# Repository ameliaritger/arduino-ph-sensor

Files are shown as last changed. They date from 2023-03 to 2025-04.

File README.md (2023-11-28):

# Arduino pH sensor 

pH sensor in the rocky intertidal during sunset

## What's in this repository?
This repository contains the scripts and files related to the development of an intertidal Arduino pH sensor.

This repository is maintained by Hofmann Lab graduate student Amelia Ritger (GitHub: [@ameliaritger](https://github.com/ameliaritger)) at the University of California, Santa Barbara in the Department of Ecology, Evolution, & Marine Biology. Please direct any questions or comments about this repository to [Amelia Ritger](mailto:aritger@ucsb.edu).

## How is this repository structured?
```
.
├── documentation/                              # folder containing documentation for building the Arduino data logger for the pH sensor project
│   └── arduinoPHConstructionOperation.docx     # document for building the Arduino data logger
|
├── software/                                   # folder containing software relevant to the Arduino data logger
|   └── arduinoCode/                            # folder containing C++ code to program the Arduino
|      └── CONFIG.h                             # configuration script, to set filename, sampling interval, and sampling start date & time
|      └── SRC.h                                # source script, for useful functions
|      └── arduinoCode.ino                      # main script, to sample from the pH sensor and store the values on the Arduino
|           
|   └── rCode/                                  # folder containing R code to process pH sensor data. Note: currently formatted for project development, not finalized for public application!
|      └── Final_OMEGAS.Rmd                     # Step 3: Apply calibration constants to deployment data
|      └── Final_Tris_Cal.Rmd                   # STEP 2: Calculate calibration constants for the sensor
|      └── Final_deploy_voltages.Rmd            # STEP 4: Plot calibrated sensor data with HOBO logger temperature data
|      └── Final_standardize_data.Rmd           # STEP 1: Standardize Arduino (new design) and Madgetech (old design) data
|
├── media/                                      # folder containing media files for project repo
|
├── draft_files/                                # folder containing all draft project files related to initial testing and development
|
├── README.md
├── .gitignore        
└── ph-sensor-dev.Rproj
```

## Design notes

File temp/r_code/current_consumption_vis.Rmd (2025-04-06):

---
title: "Data vis current consumption Version 2"
author: "Amelia Ritger"
date: "2023-10-15"
output: html_document
---

```{r setup, include=FALSE}
knitr::opts_chunk$set(echo = TRUE)
library(tidyverse)
library(janitor)
library(here)
library(ggstar)
```

Plot when adalogger is wirelessly communicating (reed switch triggered 3x) - 1) receiving data, 2) sending data, and 3) receiving data 
```{r}
receive_all <- read_csv(here("temp", "data", "power", "VoltageSet3_60V_at2023_10_14_12_19_57.csv")) %>%
  clean_names() %>%
  mutate(current_ma = current_a*10) %>%
  select(1:3, current_ma)

ggplot(receive_all, aes(x=times_s, y=current_ma)) +
  geom_line()
```

Plot "Run 1" - when Adalogger is receiving interval data
```{r}
receive_int <- read_csv(here("temp", "data", "power", "VoltageSet3_60V_at2023_10_14_12_25_20.csv")) %>%
  clean_names() %>%
  mutate(current_ma = current_a*10) %>%
  select(1:3, current_ma)

ggplot(receive_int, aes(x=times_s, y=current_ma)) +
  geom_line() +
  scale_y_continuous(limits = c(0.1,0.4),
                    breaks = seq(0, 100, by = 0.05))
```

Plot "Run 2" - when Adalogger is sending "no new data to report"
```{r}
send_no_new <- read_csv(here("temp", "data", "power", "VoltageSet3_60V_at2023_10_14_12_27_18.csv")) %>%
  clean_names() %>%
  mutate(current_ma = current_a*1000) %>%
  select(1:3, current_ma) %>%
  filter(times_s < 55) %>%
  mutate(times_s = times_s - 10) %>%
  filter(times_s>0)

receive_avg <- send_no_new %>%
  filter(times_s > 20,
         times_s < 49) %>%
  summarize(mean = mean(current_ma))  

annotation <- data.frame(
   x = c(25.56629),
   y = c(40),
   label = c("37.5 mA")
)

ggplot(send_no_new, aes(x=times_s, y=current_ma)) +
  annotate(geom = "point", x = 35.56629-10, y = 37.55524, colour = "#0072B2", size = 3) +
  geom_line() + 
  geom_text(data=annotation, aes( x=x, y=y, label=label), color="black", size=5, fontface="bold", hjust=-0.15) +
  labs(x="Time (s)", y="Current (mA)") +
  scale_y_continuous(limits = c(10,40),
                    breaks = seq(0, 100, by = 5)) +
  theme_bw() +
  theme(text = element_text(size=20))

#ggsave(here("temp", "figures", "OCEANS", "receive_data.png"), height=10, width=15, units="cm")
```

Plot "Run 3" - when Adalogger is sending  SD card data
```{r}
send_sd_a <- read_csv(here("temp", "data", "power", "VoltageSet3_60V_at2023_10_14_12_31_23.csv")) %>%
  clean_names() %>%
  mutate(current_ma = current_a*10) %>%
  select(1:3, current_ma)

ggplot(send_sd_a, aes(x=times_s, y=current_ma)) +
  geom_line() +
    scale_y_continuous(limits = c(0.1,0.4),
                     breaks = seq(0, 100, by = 0.02)) 
```

Plot "Run 4" - another ex of when Adalogger is sending SD card data
```{r}
send_sd_b <- read_csv(here("temp", "data", "power", "VoltageSet3_60V_at2023_10_14_12_34_55.csv")) %>%
  clean_names() %>%
  mutate(current_ma = current_a*1000) %>%
  select(1:3, current_ma) %>%
  filter(times_s<40)

send_avg <- send_sd_b %>%
  filter(times_s > 10,
         times_s < 19) %>%
  summarize(mean = mean(current_ma))  

annotation <- data.frame(
   x = c(31.83300, 10),
   y = c(40, 39),
   label = c("38.8 mA", "32.1 mA")
)

ggplot(send_sd_b, aes(x=times_s, y=current_ma)) +
  annotate(geom = "point", x = 31.83300, y = 38.80183, colour = "#0072B2", size = 3) +
  annotate(geom = "point", x = 11.6510231, y = 32.11241, colour = "#0072B2", size = 3) +
  geom_line() + 
  geom_text(data=annotation, aes( x=x, y=y, label=label), color="black", size=5, fontface="bold", hjust=-0.15) +
  labs(x="Time (s)", y="Current (mA)") +
  scale_y_continuous(limits = c(10,40),
                    breaks = seq(0, 100, by = 5)) +
  theme_bw() +
  theme(text = element_text(size=20))

#ggsave(here("temp", "figures", "OCEANS", "send_sd.png"), height=10, width=15, units="cm")
```

Plot when Adalogger is sampling and then sleeping
```{r}
sample_sleep_a <- read_csv(here("temp", "data", "power", "VoltageSet3_60V_at2023_10_14_14_30_00.csv")) %>%
  clean_names() %>%
  mutate(current_ma = current_a*1000) %>%
  select(1:3, current_ma) %>%
  filter(times_s>8) %>%
  mutate(times_s = times_s - 8) %>%
  filter(times_s<25)

sleep <- sample_sleep_a %>%
  filter(times_s > 5.5,
         times_s < 18.5) %>%
  summarize(mean = mean(current_ma))

sample <- sample_sleep_a %>%
  filter(times_s > 3.5,
         times_s < 5.3) %>%
  summarize(mean = mean(current_ma))

annotation <- data.frame(
   x = c(5.5,20.5, 9.95),
   y = c(0.156*100,0.135*100, 0.027*100),
   label = c("15.5 mA", "13.2 mA", "1.8 mA")
)

ggplot(sample_sleep_a, aes(x=times_s, y=current_ma)) +
  annotate(geom = "point", x = 5.4593306, y = 0.15447820*100, colour = "#0072B2", size = 3) +
  annotate(geom = "point", x = 19.884166, y = 0.13227690*100, colour = "#0072B2", size = 3) +
  annotate(geom = "point", x = 9.9521229, y = 0.01827854*100, colour = "#0072B2", size = 3) +
  geom_line() + 
  geom_text(data=annotation, aes( x=x, y=y, label=label), color="black", size=5, fontface="bold", hjust=-0.15) +
  labs(x="Time (s)", y="Current (mA)") +
  scale_y_continuous(limits = c(0,16),
                     breaks = seq(0, 100, by = 4)) +
  theme_bw() +
  theme(text = element_text(size=20))

#ggsave(here("temp", "figures", "OCEANS", "sample-sleep.png"), height=10, width=15, units="cm")
```

Plot another example of when Adalogger is sampling and then sleeping
```{r}
sample_sleep_b <- read_csv(here("temp", "data", "power", "VoltageSet3_60V_at2023_10_14_14_54_39.csv")) %>%
  clean_names() %>%
  mutate(current_ma = current_a*10) %>%
  select(1:3, current_ma) %>%
  filter(times_s<20)

annotation <- data.frame(
   x = c(14.5,4.5),
   y = c(0.16,0.15),
   label = c("0.155 mA", "0.147 mA")
)

ggplot(sample_sleep_b, aes(x=times_s, y=current_ma)) +
  annotate(geom = "point", x = 14.3918459, y = 0.15507400, colour = "#56B4E9", size = 3) +
  annotate(geom = "point", x = 4.4597836, y = 0.14704890, colour = "#56B4E9", size = 3) +
  annotate(geom = "point", x = 7.0232589, y = 0.02732002, colour = "#56B4E9", size = 3) +
  geom_line() + 
  geom_text(data=annotation, aes( x=x, y=y, label=label), color="black", size=5, fontface="bold", hjust=-0.2) +
  labs(x="Time (s)", y="Current (mA)") +
  theme_bw() +
  theme(text = element_text(size=20))
```

Merge all the plots into one!
```{r}
send_sd_b <- send_sd_b %>%
  filter(times_s < 34.739158)

send_no_new <- send_no_new %>%
  filter(times_s > 2.37331581)

all_list <- rbind(sample_sleep_a, send_sd_b, send_no_new) %>%
  mutate(time_diff = abs(times_s - lag(times_s, default = first(times_s))),
         time_diff = ifelse(time_diff > 1, 0.171, time_diff),
         time_adjust = accumulate(time_diff[-1], sum, .init = times_s[1])) %>%
  # if current_ma is less than 2, subtract 0.5697
  mutate(current_ma = ifelse(current_ma < 2, current_ma - 0.5697, current_ma)) %>%
 # if current_ma is greater than 10 and less than 15, and times_s is less than 25, subtract 0.5
  mutate(current_ma = ifelse(current_ma > 10 & current_ma < 15 & time_adjust < 25, current_ma - 0.606, current_ma))
  
annotation <- data.frame(
   x = c(15, 7, 89,56.69334, 30),
   y = c(17, 5, 39.5, 40, 25),
   label = c("12.8 mA", "1.3 mA", "37.5 mA", "38.8 mA", "32.1 mA")
)

#overwrite in-between periods with 1.26 mA sleep current 
all_list_adjust <- all_list %>%
  mutate(current_ma = ifelse(time_adjust > 24.03231 & time_adjust < 28.29884, 1.26, current_ma),
         current_ma = ifelse(time_adjust > 61.70909 & time_adjust < 66.31044, 1.26, current_ma),
         current_ma = ifelse(time_adjust > 99.10344, 1.26, current_ma))

#import image of lightning bolt
#lightning_icon <- ggimage::image_read2(here("temp", "figures", "fa-bolt.png"))

ggplot(all_list_adjust, aes(x=time_adjust, y=current_ma)) +
  annotate("rect", xmin = 2, xmax = 23, ymin = 0, ymax = 40, alpha = .1,fill = "black") +
  annotate("rect", xmin = 27, xmax = 63, ymin = 0, ymax = 40, alpha = .1,fill = "black") +
  annotate("rect", xmin = 65, xmax = 100, ymin = 0, ymax = 40, alpha = .1,fill = "black") +
  annotate("label", x = 12.5, y = 35, label = "A", fontface="bold", size = 7) +
  annotate("label", x = 45, y = 5, label = "B", fontface="bold", size = 7) +
  annotate("label", x = 82, y = 5, label = "C", fontface="bold", size = 7) +
  annotate(geom = "point", x = 56.69334, y = 38.80183, colour = "#0072B2", size = 3) +
  annotate(geom = "point", x = 36.51136, y = 32.11241, colour = "#0072B2", size = 3) +
  annotate(geom = "point", x = 82.96347, y = 37.55524, colour = "#0072B2", size = 3) +
  annotate(geom = "point", x = 19.719877, y = 12.760250, colour = "#0072B2", size = 3) +
  annotate(geom = "point", x = 9.952123, y = 1.258154, colour = "#0072B2", size = 3) +
  geom_line() + 
  geom_text(data=annotation, aes( x=x, y=y, label=label), color="black", size=5, fontface="bold", hjust=-0.15) +
  labs(x="Time (s)", y="Current (mA)") +
  scale_y_continuous(limits = c(0,40),
                    breaks = seq(0, 100, by = 5)) +
  theme_bw() +
  theme(text = element_text(size=20)) +
  #annotate("text", x = 40, y = 10, label = "Reed switch activated", fontface="bold", size = 5, hjust = 0) +
  #annotate("segment", x = 38, xend = 29, y = 8, yend = 1.5, arrow = arrow(length = unit(0.5, "cm"))) +
  geom_star(x=26.8, y=4, starshape=26, angle = -30, fill="#D55E00", size=5, colour = NA) +
  geom_star(x=64.8, y=4, starshape=26, angle = -30, fill="#D55E00", size=5, colour = NA)

#ggsave(here("temp", "figures", "FINAL(diss)", "current.png"), height=10, width=30, units="cm")
```

```{r}
sample_jan <- read_csv(here("temp", "data", "power", "VoltageSet3_6V_at2024_01_28_13_52_14.csv")) %>%
  clean_names() %>%
  mutate(current_ma = current_positive_a*1000) %>%
  select(1:2, current_ma)

ggplot(sample_jan, aes(x=times_s, y=current_ma)) +
  #annotate(geom = "point", x = 14.3918459, y = 0.15507400, colour = "#56B4E9", size = 3) +
  #annotate(geom = "point", x = 4.4597836, y = 0.14704890, colour = "#56B4E9", size = 3) +
  #annotate(geom = "point", x = 7.0232589, y = 0.02732002, colour = "#56B4E9", size = 3) +
  geom_line() + 
  #geom_text(data=annotation, aes( x=x, y=y, label=label), color="black", size=5, fontface="bold", hjust=-0.2) +
  labs(x="Time (s)", y="Current (mA)") +
  theme_bw() +
  theme(text = element_text(size=20))

sample_sleep <- sample_jan %>%
  mutate(state = ifelse(current_ma < 1.4, "sleep", 
                        ifelse(current_ma > 22, "radio", 
                               ifelse(current_ma> 10 & current_ma < 13, "sample", "other"))),
         state = ifelse(times_s > 125 & times_s < 127, "other", 
                        ifelse(times_s > 152 & times_s < 154, "other", 
                               ifelse(times_s > 182 & times_s < 185, "other", state)))) %>%
  filter(times_s>50) %>% 
  #remove last 2 data points
  slice(1:(n()-2))
  # if times_s is 125 - 127, 152-154, or 182-185 then label as "other" state

sample_sleep_group <- sample_sleep %>%
  group_by(state) %>%
  summarize(mean_current = mean(current_ma)) %>%
  ungroup() # 1.26 mA = sleep

ggplot(sample_sleep, aes(x=times_s, y=current_ma)) +
  #geom_line() + # color by sleep
  geom_point(aes(color = state)) +
  geom_line() +
  labs(x="Time (s)", y="Current (mA)") +
  theme_bw() +
  theme(text = element_text(size=20))
```

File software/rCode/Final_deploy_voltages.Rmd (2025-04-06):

---
title: "STEP 4: Plot ALL calibrated data against HOBO temperature data"
author: "Amelia Ritger"
date: "2023-04-07"
output: html_document
---

```{r setup, include=FALSE}
knitr::opts_chunk$set(echo = TRUE)
```

##Load libraries, set constants
```{r}
library(tidyverse)
library(readr)
library(janitor)
library(here)
library(lubridate)
library(scales)
library(ggpmisc)

file_names <- list.files(here("temp", "data", "raw", "deploy"), pattern = "CLEAN", recursive = FALSE, full.names = TRUE)

merged <- read_csv(file_names, col_names = TRUE) %>%
  mutate(date_lubridate=mdy(date)) %>% # tell R "date" is a DATE
  mutate(time_lubridate=hms(time)) %>% # tell R "time" is a TIME
  unite(date_time, c(date, time), sep = " ", remove = TRUE) %>% # combine the date and time columns
  mutate(date_time_lubridate=mdy_hms(date_time),
         date_time = round_date(date_time_lubridate, "5 mins")) %>%
  filter(date_time > ymd_hms("2022-12-15 17:00:00")) %>%
  mutate(v1corr = ifelse(logger=="arduino", v1-11.2, v1),
         v4corr = ifelse(logger=="arduino", v4-1.3,v4))

merged_corr_sum <- merged %>%
  group_by(logger) %>%
  summarize(meanT = mean(v4corr),
            rangeT = max(v4) - min(v4),
            meanP = mean(v1corr),
            rangeP = max(v1) - min(v1),
            sdT = sd(v4),
            sdP = sd(v1))

merged_diff <- merged %>%
  arrange(date_time) %>%
  mutate(diff_lag = abs(v4-lag(v4, default = first(v4))),
         diff_time = date_time-lag(date_time, default = first(date_time)),
         diff_temp = v4-lag(v4, default=first(v4)),
         diff_ph = v1-lag(v1, default=first(v1))) %>%
  filter(!diff_ph == 0) %>%
  group_by(logger) %>%
  summarize(meanT = mean(diff_temp),
            meanP = mean(diff_ph),
            sdT = sd(v4),
            sdP = sd(v1))

avgT <- (merged_corr_sum[[1,2]] + merged_corr_sum[[2,2]]) / 2
avgP <- (merged_corr_sum[[1,4]] + merged_corr_sum[[2,4]]) / 2

diffT <- merged_corr_sum[[1,2]] - merged_corr_sum[[2,2]]
diffP <- merged_corr_sum[[1,4]] - merged_corr_sum[[2,4]]

sd1a <- merged_diff$sdT[1]
sd1m <- merged_diff$sdT[2]

ggplot(merged, aes(x=date_time)) +
  geom_line(aes(y=v4, color=logger),size=1) +
  geom_ribbon(aes(ymin = v4 - ifelse(logger=="arduino", sd1a, sd1m), ymax = v4 + ifelse(logger=="arduino", sd1a, sd1m), fill=logger), alpha=0.2, show.legend=FALSE) +
  scale_color_manual(values=c("#D55E00", "#0072B2"), 
                     labels = c("New Design", "Old Design")) +
  scale_fill_manual(values=c("#D55E00", "#0072B2"), 
                     labels = c("New Design", "Old Design")) +
  #scale_color_brewer(palette="Set1", direction=-1, labels = c("New Design", "Old Design")) +
  #scale_fill_brewer(palette="Set1", direction=-1, labels = c("New Design", "Old Design")) +
  labs(x="Date and Time", y="Temperature (mV)", color = "") +
  scale_x_datetime(breaks = scales::date_breaks("4 hours"), 
                   labels = date_format("%d %b %Y %H:%M")) +
  theme_bw() +
  theme(axis.text.x=element_text(angle=20, vjust = 1, hjust=1),
        legend.position = "top", 
        legend.text = element_text(size=10))

#ggsave(here("temp", "figures", "FINAL(diss)", "temp-deploy.png"), height=10, width=15, units="cm")
```

```{r}
#Subset it for the swap time
merged_diff <- merged %>%
  arrange(date_time) %>%
  mutate(diff_lag = abs(v4-lag(v4, default = first(v4))),
         diff_time = date_time-lag(date_time, default = first(date_time)),
         diff_temp = v4-lag(v4, default=first(v4)),
         diff_ph = v1-lag(v1, default=first(v1))) %>%
  filter(!diff_ph == 0) #%>%
  #group_by(logger) %>%
  summarize(meanT = mean(diff_temp),
            meanP = mean(diff_ph),
            sdT = sd(v4),
            sdP = sd(v1))

ggplot(merged_diff, aes(x=date_time)) +
  geom_point(aes(y=diff_ph, color=logger))
```

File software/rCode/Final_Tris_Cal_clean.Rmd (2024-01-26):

---
title: "STEP 2: Calculate Tris calibration constants for DuraFET"
author: "Amelia Ritger"
date: "2024-01-25"
output: html_document
---

```{r setup, include=FALSE}
knitr::opts_chunk$set(echo = TRUE)
```

##Load libraries, set constants
```{r}
library(tidyverse)
library(readr)
library(janitor)
library(here)
library(lubridate)

filename <- "0125tris_clean" #filename for tris data
row_remove <- 15 # number of rows to remove from beginning of data frame
```

## Run "Ideal" calibration for DuraFET
```{r}
var_ard <- 0 #calculated uncertainties using raw data

ard_correction_m <- 1 #slope coefficient for arduino (corrected with HOBO)
ard_correction_b <- 0

trisdata <- read_csv(here("temp", "data", "jan2024", paste(filename,".csv",sep=""))) %>%
  mutate(date = mdy(date),
           time = hms(time),
           date_time = paste(date, time),
           date_time_lubridate=ymd_hms(date_time)) %>%
  select(date_time_lubridate, v1, v2, v3, v4) %>%
  rename(date_time = date_time_lubridate)

tris_voltages <- data.frame(trisdata$v1,trisdata$v2,trisdata$v3,trisdata$v4) %>% # create OMEGAS data frame with the raw voltages
  mutate(mv1=as.numeric(trisdata.v1),
         mv2=as.numeric(trisdata.v2),
         mv3=as.numeric(trisdata.v3),
         mv4=as.numeric(trisdata.v4)) %>% # changing data to numeric arguments
  select(mv1, mv2, mv3, mv4) # cleaning data frame

omegas_temp_tris <- tris_voltages %>% # create new data frame using omegas values
  mutate(v1=(mv1/1000),
         v2=(mv2/1000),
         v3=(mv3/1000),
         v4=(mv4/1000)) %>% # converting the mV to volts
  mutate(vbattery=((abs(v3)/100)*101.57)) %>% # calculate vbattery
  mutate(z=(v4/100)+vbattery*((15000*1)/((1000000*1)+(15000*1)))) %>% # calculate column k
  mutate(y=(z*(1000000*1))) %>% # calculate column l
  mutate(rthermistor=(y/(vbattery-z))) %>% # calculate Rthermistor
  mutate(sh_a=as.numeric(0.00106329736674527)) %>% # create column with Steinhart constant A
  mutate(sh_b=as.numeric(0.000251377462346306)) %>% # create column with Steinhart constant B
  mutate(sh_c=as.numeric(2.55455247726963E-08)) %>% # create column with Steinhart constant C
  mutate(k=(1/(sh_a+sh_b*log(rthermistor)+sh_c*(log(rthermistor))^3))) %>% # create column to calculate intermediate value K
  mutate(durafet=as.numeric((k-273.15))) %>% # create new column to calculate durafet therm
  mutate(calt=as.numeric(1.0086*durafet+0.3157)) # create Cal_T column (does not get used for further calibration)

temp <- c(omegas_temp_tris$durafet) # copy durafet therm into tris pH template
b <- as.numeric(rep("11911.08",length(temp))) # create vector for tris pH template column b
c <- as.numeric(rep("18.2499",length(temp))) # create vector for tris pH template column c
d <- as.numeric(rep("0.039336",length(temp))) # create vector for tris pH template column d
e <- as.numeric(rep("366.27059",length(temp))) # create vector for tris pH template column e
f <- as.numeric(rep("0.53993607",length(temp))) # create vector for tris pH template column f
g <- as.numeric(rep("0.00016329",length(temp))) # create vector for tris pH template column g
h <- as.numeric(rep("64.52243",length(temp))) # create vector for tris pH template column h
i <- as.numeric(rep("0.084041",length(temp))) # create vector for tris pH template column i
j <- as.numeric(rep("0.11149858",length(temp))) # create vector for tris pH template column j
k <- as.numeric(rep("273.15",length(temp))) # create vector for tris pH template column k
t <- as.numeric(rep(k+temp),length(temp)) # create vector for tris pH template column t
m <- as.numeric(rep("35",length(temp))) # create vector for tris pH template column m

tris_ph_template <- data.frame(temp,b,c,d,e,f,g,h,i,j,t,k,m)%>% # create tris pH template as a data frame with all above columns
  mutate(n=(b-(c*m)-(d*m*m))*1/t) %>% # create column n
  mutate(o=(-e+(f*m)+(g*m*m))) %>% # create column o
  mutate(p=(h-(i*m))*log(t)-(j*(t))) %>% # create column p
  mutate(trisph=(n+o+p)) # calculate tris pH, add as a new column to tris pH template data frame

omegas_ph_tris <- data.frame(trisdata$date_time,omegas_temp_tris$durafet,omegas_temp_tris$v1) %>% # create data frame with durafet therm and voltage 1 values
  mutate(trisph=tris_ph_template$trisph) %>% # add tris pH values into calibration dataframe 
  mutate(tk=omegas_temp_tris$durafet+273.15) %>% # add TK column to data frame
  mutate(st=(8.31451*tk/96487*log(10))) %>% # add S(T) column to data frame
  mutate(eot=(-0.374911706-(0.001*(tk-290.2751473)))) %>% # add Eo(T) column to data frame
  mutate(omegasph=(omegas_temp_tris$v1-eot)/st) %>% # add pH column to data frame
  mutate(diff=(trisph-omegasph)) %>% # add difference column (tris pH - omegas pH) to data frame
  mutate(tempdiff=abs(omegas_temp_tris.durafet-lag(omegas_temp_tris.durafet,n=5,default=first(omegas_temp_tris.durafet)))) %>% # find difference between two temp measurements 5 rows apart to identify where temperature stabilizes
  mutate(phdiff=abs(omegasph-lag(omegasph,n=5,default=first(omegasph)))) # find difference between two pH measurements 5 rows apart to identify where pH stabilizes

calibration_values <- omegas_ph_tris %>% # work in omegas_calibration dataframe
  filter(row_number()!=c(1:row_remove)) %>% # remove the first 100 rows (first 20 minutes of data)
  slice_min(tempdiff,n=10) %>% # select the rows that contains the minimum values of change in temperature over time 
  slice_min(phdiff,n=1) %>% # select the row that contains the minimum value of change in pH over time in within the 10 lowest temp differences
  mutate(diff_omegasph = (omegasph - mean(omegasph))) %>%
  slice_min(diff_omegasph) %>%
  slice(1L)

#Write out .csv files
write.csv(omegas_ph_tris, here("temp", "data", "jan2024", paste(filename,"_omegas.csv", sep="")),row.names = FALSE) # create csv with calibrated values
write.csv(calibration_values, here("temp", "data", "jan2024", paste(filename,"_omegas_calib.csv", sep="")),row.names=FALSE)
```

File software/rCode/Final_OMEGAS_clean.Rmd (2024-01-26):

---
title: "STEP 3: Apply GREEN and RED calibration data to all readings"
author: "Amelia Ritger"
date: "2023-04-07"
output: html_document
---

```{r setup, include=FALSE}
knitr::opts_chunk$set(echo = TRUE)
```

##Load libraries, set constants
```{r}
library(tidyverse)
library(readr)
library(janitor)
library(here)
library(lubridate)

filename_calib <- "0125tris_clean_omegas_calib" #filename for tris calibration data
filename_deploy <- "0123comp_clean" #filename for deployment calibration data
```

## Run calibration for GREEN data
```{r}
calibration_values <- read_csv(here("temp", "data", "jan2024", paste(filename_calib,".csv",sep=""))) %>%
  rename("durafet_temp" = "omegas_temp_tris.durafet",
         "v1" = "omegas_temp_tris.v1")

rawdata <- read_csv(here("temp", "data", "jan2024", paste(filename_deploy,".csv",sep=""))) %>%
    mutate(date = mdy(date),
           time = hms(time),
           date_time = paste(date, time),
           date_time_lubridate=ymd_hms(date_time)) %>%
  select(date_time_lubridate, v1, v2, v3, v4) %>%
  rename(date_time = date_time_lubridate)

raw_voltages <- data.frame(rawdata$v1,rawdata$v2,rawdata$v3,rawdata$v4) %>% # create OMEGAS data frame with the raw voltages
  mutate(mv1=as.numeric(rawdata.v1),
         mv2=as.numeric(rawdata.v2),
         mv3=as.numeric(rawdata.v3),
         mv4=as.numeric(rawdata.v4)) %>% # changing data to numeric arguments
  select(mv1, mv2, mv3, mv4) # cleaning data frame

omegas_temp_raw <- raw_voltages %>% # create OMEGAS data frame with the raw voltages
  mutate(v1=(mv1/1000),
         v2=(mv2/1000),
         v3=(mv3/1000),
         v4=(mv4/1000)) %>% # converting the mV to volts
  mutate(vbattery=((abs(v3)/100)*101.57)) %>% # calculate vbattery
  mutate(z=(v4/100)+vbattery*((15000*1)/((1000000*1)+(15000*1)))) %>% # calculate column k
  mutate(y=(z*(1000000*1))) %>% # calculate column l
  mutate(rthermistor=(y/(vbattery-z))) %>% # calculate Rthermistor
  mutate(sh_a=as.numeric(0.00106329736674527)) %>% # create column with Steinhart constant A
  mutate(sh_b=as.numeric(0.000251377462346306)) %>% # create column with Steinhart constant B
  mutate(sh_c=as.numeric(2.55455247726963E-08)) %>% # create column with Steinhart constant C
  mutate(k=(1/(sh_a+sh_b*log(rthermistor)+sh_c*(log(rthermistor))^3))) %>% # create column to calculate intermediate value K
  mutate(durafet=as.numeric((k-273.15))) # create new column to calculate durafet therm

temp <- c(omegas_temp_raw$durafet) # copy durafet therm into tris pH template
b <- as.numeric(rep("11911.08",length(temp))) # create vector for tris pH template column b
c <- as.numeric(rep("18.2499",length(temp))) # create vector for tris pH template column c
d <- as.numeric(rep("0.039336",length(temp))) # create vector for tris pH template column d
e <- as.numeric(rep("366.27059",length(temp))) # create vector for tris pH template column e
f <- as.numeric(rep("0.53993607",length(temp))) # create vector for tris pH template column f
g <- as.numeric(rep("0.00016329",length(temp))) # create vector for tris pH template column g
h <- as.numeric(rep("64.52243",length(temp))) # create vector for tris pH template column h
i <- as.numeric(rep("0.084041",length(temp))) # create vector for tris pH template column i
j <- as.numeric(rep("0.11149858",length(temp))) # create vector for tris pH template column j
k <- as.numeric(rep("273.15",length(temp))) # create vector for tris pH template column k
t <- as.numeric(rep(k+temp),length(temp)) # create vector for tris pH template column t
m <- as.numeric(rep("35",length(temp))) # create vector for tris pH template column m

raw_tris_ph <- data.frame(temp,b,c,d,e,f,g,h,i,j,t,k,m) %>% # create tris pH template as a data frame with all above columns
  mutate(n=(b-(c*m)-(d*m*m))*1/t) %>% # create column n
  mutate(o=(-e+(f*m)+(g*m*m))) %>% # create column o
  mutate(p=(h-(i*m))*log(t)-(j*(t))) %>% # create column p
  mutate(trisph=(n+o+p)) # calculate tris pH, add as a new column to tris pH template data frame

omegas_ph_raw <- data.frame(rawdata$date_time,omegas_temp_raw$durafet,omegas_temp_raw$v1) %>%
   # create data frame with durafet therm and voltage 1 values
  rename(date_time=rawdata.date_time) %>% # rename date/time column from trisdata data frame
  mutate(trisph=raw_tris_ph$trisph) %>% # add tris pH values into calibration dataframe TRIS PH IS NOT THE SAME LENGTH AS THE RAW DATA
  mutate(tk=omegas_temp_raw$durafet+273.15) %>% # add TK column to data frame
  mutate(st=(8.31451*tk/96487*log(10))) %>% # add S(T) column to data frame
  mutate(eo=((calibration_values$v1)-(calibration_values$trisph)*8.31451*(273.15+calibration_values$durafet_temp)*log(10)/96487)) %>% # calculate eo value using calibration values
  mutate(eot=(eo-(0.001*(tk-(273.15+calibration_values$durafet_temp))))) %>% # add Eo(T) column to data frame
  mutate(omegasrawph=(omegas_temp_raw$v1-eot)/st) %>% # add pH column to data frame
  mutate(diff=(trisph-omegasrawph)) # add difference column (tris pH - omegas pH) to data frame

raw_calibrated <- omegas_ph_raw %>% # create new dataframe using omegasph_raw data
  select(date_time, omegas_temp_raw.durafet, omegasrawph) %>% # keep only date/time, temperature, and pH columns
  rename("p_h"=3)

#Write .csv
write.csv(raw_calibrated, here("temp", "data", "jan2024", paste("FINAL_arduino.csv")),row.names = FALSE) # create csv with calibrated values

```

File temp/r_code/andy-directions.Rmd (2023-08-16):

---
title: "Untitled"
author: "Amelia Ritger"
date: "2023-04-10"
output: html_document
---

```{r setup, include=FALSE}
knitr::opts_chunk$set(echo = TRUE)
```

fit difference in temperature at each point 

the standard deviation of the temperature in the ICE bath and the 25C bath is what you want to calculate

subtract HOBO temp from Durafet temp, get standard deviation of that. do it for each temperature. 
are there significant differences between each temp.

that's my temperature uncertainty.

Take all my raw data and get the list of file names
```{r}

```

How much can temp change if R1 is at top of the range
```{r}

```

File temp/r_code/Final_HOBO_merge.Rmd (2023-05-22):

---
title: "STEP 4: Plot ALL calibrated data against HOBO temperature data"
author: "Amelia Ritger"
date: "2023-04-07"
output: html_document
---

```{r setup, include=FALSE}
knitr::opts_chunk$set(echo = TRUE)
```

##Load libraries, set constants
```{r}
library(tidyverse)
library(readr)
library(janitor)
library(here)
library(lubridate)
library(scales)
library(ggpmisc)

#pattern_ignore = "calib" #ignore calibration value files
#file_names <- list.files(here("data", "calibrated"), pattern = "*.csv", recursive = FALSE, full.names = TRUE)
#file_ignore <- list.files(here("data", "calibrated"), pattern = pattern_ignore, recursive = FALSE, full.names = TRUE)
#file_names <- setdiff(file_names, file_ignore)

file_names <- list.files(here("data", "calibrated"), pattern = "OMEGAS_CLEAN", recursive = FALSE, full.names = TRUE)

merged <- read_csv(file_names, col_names = TRUE) %>%
  mutate(date_time = round_date(date_time, "15 seconds"))
```

Load and merge hobo logger data
```{r}
temp1 <- read_csv(here("data", "temp", "Apr8_lab.csv"), col_names = TRUE)
temp2 <- read_csv(here("data", "temp", "Apr9_lab.csv"), col_names = TRUE) 
temp4 <- read_csv(here("data", "temp", "Apr12_lab_newhobo.csv"), col_names = TRUE) 
temp5 <- read_csv(here("data", "temp", "Apr11_lab_newhobo.csv"), col_names = TRUE) 
temp6 <- read_csv(here("data", "temp", "Apr10_lab_newhobo_overnight.csv"), col_names = TRUE) 

temp3 <- rbind(temp1, temp2, temp4, temp5, temp6) 

temp <- temp3 %>%
  select(2:3) %>%
  setNames(c("date_time", "hobo_temp")) %>%
  mutate(date_time=mdy_hms(date_time)) %>%
  mutate(date_time = round_date(date_time, "5 seconds"))

#ggplot(temp, aes(x=date_time)) +
#  geom_point(aes(y=hobo_temp))
```

```{r}
# #4/8 and 4/9 data
# temp_room <- temp %>%
#   filter(date_time < ymd_hms("2023-04-08 05:00:00")) %>%
#   filter(date_time > ymd_hms("2023-04-08 04:25:00"))
# 
# temp_hot <- temp %>%
#   filter(date_time > ymd_hms("2023-04-08 15:00:00")) %>%
#   filter(date_time < ymd_hms("2023-04-08 15:30:00"))
# 
# temp_cold <- temp %>%
#   filter(date_time > ymd_hms("2023-04-09 16:00:00")) %>%
#   filter(date_time < ymd_hms("2023-04-09 16:20:00"))
# 
# ####4/10 data
# temp_room <- temp %>%
#   filter(date_time > ymd_hms("2023-04-11 06:22:00")) %>%
#   filter(date_time < ymd_hms("2023-04-11 06:50:00"))
# 
# temp_hot <- temp %>%
#   filter(date_time > ymd_hms("2023-04-10 15:44:00")) %>%
#   filter(date_time < ymd_hms("2023-04-10 15:52:00"))
# 
# temp_cold <- temp %>%
#   filter(date_time > ymd_hms("2023-04-10 13:20:00")) %>%
#   filter(date_time < ymd_hms("2023-04-10 13:28:00"))
# 
# ggplot(data = temp_room, aes(x=date_time)) +
#   geom_point(aes(y=hobo_temp))
# 
# ggplot(data = temp_room, aes(x=date_time)) +
#   geom_point(aes(y=hobo_temp)) +
#   geom_point(data = temp_hot, aes(y=hobo_temp)) +
#   geom_point(data = temp_cold, aes(y=hobo_temp))
```

```{r}
merged_all <- full_join(merged, temp) %>%
  filter(!is.na(durafet_temp)) %>%
  mutate(diff_temp = hobo_temp - durafet_temp)

# merged_sd <- merged_all %>%
#   mutate(temp_diff = abs(durafet_temp - hobo_temp)) %>%
#   filter(temp_diff<6)
# 
# ggplot(merged_sd, aes(x=date_time, group=durafet)) +
#   geom_point(aes(y=durafet_temp, color=durafet)) +
#   geom_point(aes(y=hobo_temp), color="black")
# 
# merged_sd_sum <- merged_sd %>%
#   group_by(logger) %>%
#   summarize(mean = mean(temp_diff),
#             sd = sd(temp_diff))
# 
# ggplot(merged_sd, aes(x=temp_diff)) +
#   geom_histogram()
#%>%
#  filter(date_time > ymd_hms("2023-04-10 09:00:00")) %>%
#  mutate(logger=ifelse(durafet=="green", "madgetech1", "madgetech2"))
  
  #%>% #remove HOBO data without DuraFET measurements
  #mutate(hobo_temp = ifelse(date_time > ymd_hms("2023-04-09 16:00:00"), hobo_temp - 4.2, hobo_temp))
  
ggplot(merged_all, aes(x=date_time, group=logger)) +
  geom_point(aes(y=durafet_temp, color=logger))

merged_sub <- merged_all %>%
  filter(date_time > ymd_hms("2023-04-11 12:00:00"), date_time < ymd_hms("2023-04-12 06:00:00"))

ggplot(merged_sub, aes(x=date_time)) +
  geom_point(aes(y=durafet_temp, color=logger))

#ggsave(here("figures", "final", "all_correction.png"))
```

CALCULATE SD AT DIFF "stable" TEMPS
```{r}
merged_room <- merged_all %>%
  filter(date_time < ymd_hms("2023-04-08 03:00:30"), date_time > ymd_hms("2023-04-08 01:00:00"))

ggplot(merged_room, aes(x=date_time)) +
  geom_point(aes(y=durafet_temp, color=logger))

merged_room_sd <- merged_room %>%
  group_by(logger) %>%
  summarize(mean = mean(durafet_temp),
            sd = sd(durafet_temp),
            mean_diff = mean(diff_temp),
            sd_diff = sd(diff_temp))

merged_hot <- merged_all %>%
  filter(date_time > ymd_hms("2023-04-11 15:00:00"), date_time < ymd_hms("2023-04-11 18:00:00"))

ggplot(merged_hot, aes(x=date_time)) +
  geom_point(aes(y=durafet_temp, color=logger))

merged_hot_sd <- merged_hot %>%
  group_by(logger) %>%
  summarize(mean = mean(durafet_temp),
            sd = sd(durafet_temp),
            mean_diff = mean(diff_temp),
            sd_diff = sd(diff_temp))

merged_cold <- merged_all %>%
  filter(date_time < ymd_hms("2023-04-09 18:00:00"), date_time > ymd_hms("2023-04-09 15:00:00"))

ggplot(merged_cold, aes(x=date_time)) +
  geom_point(aes(y=durafet_temp, color=logger))

merged_cold_sd <- merged_cold %>%
  group_by(logger) %>%
  summarize(mean = mean(durafet_temp),
            sd = sd(durafet_temp),
            mean_diff = mean(diff_temp),
            sd_diff = sd(diff_temp))

#write.csv(merged_cold, here("data", "cold_temp.csv"),row.names = FALSE)

```

```{r}
merged_room <- merged_all %>%
  filter(date_time > ymd_hms("2023-04-11 06:22:00")) %>%
  filter(date_time < ymd_hms("2023-04-11 06:50:00"))
  #filter(date_time < ymd_hms("2023-04-12 11:15:00"))

ggplot(data = merged_room, aes(x=date_time)) +
  geom_point(aes(y=hobo_temp)) +
  geom_point(aes(y=durafet_temp, color = durafet))

merged_hot <- merged_all %>%
  filter(date_time > ymd_hms("2023-04-10 15:44:00")) %>%
  filter(date_time < ymd_hms("2023-04-10 15:52:00"))
  #filter(date_time > ymd_hms("2023-04-12 16:45:00"))

ggplot(data = merged_hot, aes(x=date_time)) +
  geom_point(aes(y=hobo_temp)) +
  geom_point(aes(y=durafet_temp, color = durafet))

merged_cold <- merged_all %>%
  filter(date_time > ymd_hms("2023-04-10 13:20:00")) %>%
  filter(date_time < ymd_hms("2023-04-10 13:28:00"))
  #filter(date_time > ymd_hms("2023-04-12 12:45:00"), date_time < ymd_hms("2023-04-12 15:30:00"))

ggplot(data = merged_cold, aes(x=date_time)) +
  geom_point(data = merged_cold, aes(y=hobo_temp)) +
  geom_point(data = merged_cold, aes(y=durafet_temp, color = durafet))

ggplot(data = merged_room, aes(x=date_time)) +
  geom_point(aes(y=durafet_temp, color = durafet)) +
  geom_point(aes(y=hobo_temp)) +
  geom_point(data = merged_hot, aes(y=hobo_temp)) +
  geom_point(data = merged_hot, aes(y=durafet_temp, color = durafet)) +
  geom_point(data = merged_cold, aes(y=hobo_temp)) +
  geom_point(data = merged_cold, aes(y=durafet_temp, color = durafet))

#ggsave(here("figures", "final", "cold-fake.png"))

#write.csv(merged_all, here("data", "merged_all.csv"), row.names=FALSE)
```

Find difference between GREEN/RED durafet and HOBO temp to calculate temperature correction
```{r}
merged_diff_room <- merged_all %>%
  mutate(temp_diff = hobo_temp - durafet_temp) %>%
  #filter(date_time < ymd_hms("2023-04-12 11:15:00")) %>%
  filter(date_time > ymd_hms("2023-04-11 06:22:00")) %>%
  filter(date_time < ymd_hms("2023-04-11 06:50:00")) %>%
  #filter(date_time < ymd_hms("2023-04-08 05:00:00")) %>%
  #filter(date_time > ymd_hms("2023-04-08 04:25:00")) %>%
  group_by(durafet) %>%
  summarize(mean_temp_diff = mean(temp_diff),
            mean_temp = mean(durafet_temp),
            mean_h_temp = mean(hobo_temp))

merged_diff_hot <- merged_all %>%
  mutate(temp_diff = hobo_temp - durafet_temp) %>%
  #filter(date_time > ymd_hms("2023-04-12 16:45:00")) %>%
  filter(date_time > ymd_hms("2023-04-10 15:44:00")) %>%
  filter(date_time < ymd_hms("2023-04-10 15:52:00")) %>%
  #filter(date_time > ymd_hms("2023-04-08 15:00:00")) %>%
  #filter(date_time < ymd_hms("2023-04-08 15:30:00")) %>%
  group_by(durafet) %>%
  summarize(mean_temp_diff = mean(temp_diff),
            mean_temp = mean(durafet_temp),
            mean_h_temp = mean(hobo_temp))

merged_diff_cold <- merged_all %>%
  mutate(temp_diff = hobo_temp - durafet_temp) %>%
    #filter(date_time > ymd_hms("2023-04-12 12:45:00"), date_time < ymd_hms("2023-04-12 15:30:00")) %>%
  filter(date_time > ymd_hms("2023-04-10 13:20:00")) %>%
  filter(date_time < ymd_hms("2023-04-10 13:28:00")) %>%
  #filter(date_time > ymd_hms("2023-04-09 16:00:00")) %>%
  #filter(date_time < ymd_hms("2023-04-09 16:20:00")) %>%
  group_by(durafet) %>%
  summarize(mean_temp_diff = mean(temp_diff),
            mean_temp = mean(durafet_temp),
            mean_h_temp = mean(hobo_temp)) 

merged_temp <- rbind(merged_diff_hot, merged_diff_room, merged_diff_cold)

ggplot(merged_temp, aes(x=mean_h_temp, y=mean_temp_diff, group=durafet, color=durafet)) +
  geom_point() +
  stat_poly_line(se=F) +
  stat_poly_eq(aes(label = paste(after_stat(eq.label))))

ggsave(here("figures", "final", "profit-MADGETECH-hobotemp.png"))
```

```{r}
merged_cold <- merged_all %>%
  #filter(date_time < ymd_hms("2023-04-07 16:00:00")) %>%
  #filter(date_time > ymd_hms("2023-04-07 15:00:00"))
  filter(date_time > ymd_hms("2023-04-08 01:00:00")) %>%
  filter(date_time < ymd_hms("2023-04-08 16:00:00"))
  #filter(date_time > ymd_hms("2023-04-07 13:00:00"))

ggplot(merged_cold, aes(x=date_time)) +
  geom_point(aes(y=p_h, color=logger))
```

```{r}
merged_swap <- merged_all %>%
  #filter(date_time > ymd_hms("2023-04-11 12:00:00"), date_time < ymd_hms("2023-04-11 14:55:00")) %>%
  filter(date_time < ymd_hms("2023-04-09 18:00:00"), date_time > ymd_hms("2023-04-09 15:00:00")) #for ARD vs MAD 4/9
  #mutate(logger = ifelse(date_time < ymd_hms("2023-04-11 14:55:00"), "madgetech_comp", logger),
  #       logger = ifelse(date_time > ymd_hms("2023-04-11 13:45:00") & logger == "madgetech_comp" & durafet == "green", "Madgetech-1",
  #                       ifelse(date_time > ymd_hms("2023-04-11 13:45:00") & logger == "madgetech_comp" & durafet == "red", "Madgetech-2",
  #                              ifelse(date_time < ymd_hms("2023-04-11 13:45:00") & logger == "madgetech_comp" & durafet == "green","Madgetech-2",
  #                                     ifelse(date_time < ymd_hms("2023-04-11 13:45:00") & logger == "madgetech_comp" & durafet == "red","Madgetech-1",logger)))))
  #filter(date_time < ymd_hms("2023-04-10 01:00:00")) %>%
  #filter(date_time > ymd_hms("2023-04-09 13:45:00")) %>%
  #filter(date_time < ymd_hms("2023-04-09 17:00:00")) %>%
  #filter(date_time < ymd_hms("2023-04-09 14:40:00") | date_time > ymd_hms("2023-04-09 14:47:00"))

ggplot(merged_swap, aes(x=date_time)) +
  geom_point(aes(y=p_h, color=logger)) +
  #geom_point(aes(y=hobo_temp)) +
  labs(x="Date and Time", y="pH", color = "") +
  scale_x_datetime(breaks = scales::date_breaks("30 min"), 
                   labels = date_format("%Y-%m-%d %H:%M")) +
  scale_color_brewer(palette="Set1", direction=-1, labels = c("New Design", "Old Design", "Madgetech #1", "Madgetech #2")) +
  theme_bw() +
  theme(axis.text.x=element_text(angle=20, vjust = 1, hjust=1),
        legend.position = "top")

#ggsave(here("figures", "final", "swapday_ph.png"))
```

```{r}
merge_swap_diff <- merged_swap %>%
  arrange(date_time) %>%
  group_by(logger) %>%
  mutate(diff_lag = abs(durafet_temp-lag(durafet_temp, default = first(durafet_temp)))) %>%
  filter(#!diff_lag > 0.2,
         #!diff_lag == 0) %>%
         !diff_lag > 0.05) %>% #remove lag values associated with start time
  ungroup()

ggplot(merge_swap_diff, aes(x=date_time)) +
  geom_point(aes(y=diff_lag, color=logger))
```

```{r}
merged_diff <- merge_swap_diff %>%
  mutate(period = ifelse(date_time <= ymd_hms("2023-04-09 16:00:00"), 1, 2)) %>% #for ARD vs MAD 4/9 comparison
  #mutate(period = ifelse(date_time<=ymd_hms("2023-04-11 13:45:00"), "1", "2")) %>%
  arrange(date_time) %>%
  group_by(period) %>%
  mutate(diff_time = date_time-lag(date_time, default = first(date_time)),
         diff_temp = durafet_temp-lag(durafet_temp, default=first(durafet_temp)),
         diff_ph = p_h-lag(p_h, default=first(p_h))) %>%
  filter(!diff_ph == 0) %>%
         #diff_temp = ifelse(diff_time>0, NA, durafet_temp-lag(durafet_temp, default=first(durafet_temp))),
         #diff_ph = ifelse(diff_time>0, NA, p_h-lag(p_h, default=first(p_h)))) %>%
  #filter(diff_ph < -0.1 | diff_ph > 0.1) %>%
  ungroup() #%>%
  #slice(3:n()) %>%
  #filter(!date_time == ymd_hms("2023-04-09 16:05:15"))
  ## DO BELOW ONLY FOR GRAPHS!!!!!!!!!!!!!!!!!!!!!!!!!!!!!!!!
  #mutate(logger = ifelse(logger == "Madgetech-2", "madgetech", logger))

merged_diff_sum <- merged_diff %>%
  group_by(period, logger) %>%
  summarize(mean_temp = mean(durafet_temp),
            #sd_temp = sd(durafet_temp),
            mean_ph = mean(p_h),
            #sd_ph = sd(p_h),
            mean_diff_t = mean(diff_temp),
            mean_diff_p = mean(diff_ph))

avg_t_1 <- abs(mean(merged_diff_sum[[1,5]], merged_diff_sum[[2,5]]))
avg_t_2 <- abs(mean(merged_diff_sum[[3,5]], merged_diff_sum[[4,5]]))
#avg_t_1 <- abs(mean(merged_diff_sum[[5,5]], merged_diff_sum[[6,5]]))
#avg_t_2 <- abs(mean(merged_diff_sum[[7,5]], merged_diff_sum[[8,5]]))
avg_temp <- avg_t_1-avg_t_2

avg_p_1 <- abs(mean(merged_diff_sum[[1,6]], merged_diff_sum[[2,6]]))
avg_p_2 <- abs(mean(merged_diff_sum[[3,6]], merged_diff_sum[[4,6]]))
#avg_p_1 <- abs(mean(merged_diff_sum[[5,6]], merged_diff_sum[[6,6]]))
#avg_p_2 <- abs(mean(merged_diff_sum[[7,6]], merged_diff_sum[[8,6]]))
avg_ph <- avg_p_2-avg_p_1

period1 <- merged_diff %>%
  filter(period==1)
period2 <- merged_diff %>%
  filter(period==2)
#period3 <- merged_diff %>%
#  filter(period==3)
#period4 <- merged_diff %>%
#  filter(period==4)

ggplot(data=merged_diff, aes(x=date_time)) +
  geom_line(data=period1, aes(y=diff_temp, color=logger), size=1) +
  geom_line(data=period2, aes(y=diff_temp, color=logger), size=1) +
  #geom_line(data=period3, aes(y=diff_ph, color=logger), size=1) +
  #geom_line(data=period4, aes(y=diff_ph, color=logger), size=1) +
  
  annotate("text", y=0, x=ymd_hms("2023-04-09 15:30:00"), label="Mean = 0.7") +
  geom_segment(aes(x=ymd_hms("2023-04-09 15:30:00"), xend=ymd_hms("2023-04-09 15:30:00"), y = 0.2, yend = 0.5), arrow = arrow(length = unit(0.5, "cm"))) +
  geom_segment(aes(x=ymd_hms("2023-04-09 15:30:00"), xend=ymd_hms("2023-04-09 15:30:00"), y = -0.2, yend = -0.5), arrow = arrow(length = unit(0.5, "cm"))) +

  annotate("text", y=0, x=ymd_hms("2023-04-09 16:40:00"), label="Mean = 0.9") +
  geom_segment(aes(x=ymd_hms("2023-04-09 16:40:00"), xend=ymd_hms("2023-04-09 16:40:00"), y = 0.2, yend = 0.5), arrow = arrow(length = unit(0.5, "cm"))) +
  geom_segment(aes(x=ymd_hms("2023-04-09 16:40:00"), xend=ymd_hms("2023-04-09 16:40:00"), y = -0.2, yend = -0.5), arrow = arrow(length = unit(0.5, "cm"))) +
  labs(x="Date and Time", y="Temperature difference (C)", color = "") +
  
  scale_x_datetime(breaks = scales::date_breaks("30 min"), 
                   labels = date_format("%d %b %Y %H:%M")) +
  scale_color_brewer(palette="Set1", direction=-1, labels = c("New Design", "Old Design")) +
  #scale_color_manual(values=c("#E69F00", "#da0018"),labels = c("Old Design #1", "Old Design #2")) +
  #scale_color_manual(values=c("#D55E00", "#0072B2","#56B4E9"),labels = c("New Design", "Old Design", "Old Design"), guide = guide_legend(reverse = TRUE)) +
  theme_bw() +
  theme(axis.text.x=element_text(angle=20, vjust = 1, hjust=1),
        legend.position = "top")

ggsave(here("figures", "final", "temp-differenceARD.png"), height=10, width=15, units="cm")
```

```{r}
ggplot(data=merged_diff, aes(x=date_time)) +
  geom_line(data=period1, aes(y=diff_temp, color=logger), size=1) +
  geom_line(data=period2, aes(y=diff_temp, color=logger), size=1) +
  geom_line(data=period3, aes(y=diff_temp, color=logger), size=1) +
  geom_line(data=period4, aes(y=diff_temp, color=logger), size=1) +
  
  annotate("text", y=0, x=ymd_hms("2023-04-11 13:15:00"), label="Mean = 0.40") +
  geom_segment(aes(x=ymd_hms("2023-04-11 13:15:00"), xend=ymd_hms("2023-04-11 13:15:00"), y = 0.1, yend = 0.3), arrow = arrow(length = unit(0.5, "cm"))) +
  geom_segment(aes(x=ymd_hms("2023-04-11 13:15:00"), xend=ymd_hms("2023-04-11 13:15:00"), y = -0.1, yend = -0.3), arrow = arrow(length = unit(0.5, "cm"))) +
  labs(x="Date and Time", y="Temperature difference (C)", color = "") +
  
  annotate("text", y=0.8, x=ymd_hms("2023-04-11 14:15:00"), label="Mean = 0.30") +
  geom_segment(aes(x=ymd_hms("2023-04-11 14:15:00"), xend=ymd_hms("2023-04-11 14:15:00"), y = 0.7, yend = 0.4), arrow = arrow(length = unit(0.5, "cm"))) +
  #geom_segment(aes(x=ymd_hms("2023-04-11 14:15:00"), xend=ymd_hms("2023-04-11 14:15:00"), y = -0.2, yend = -0.9), arrow = arrow(length = unit(0.5, "cm"))) +
  labs(x="Date and Time", y="pH difference", color = "") +
  
  annotate("text", y=0.8, x=ymd_hms("2023-04-11 15:25:00"), label="Mean = 0.02") +
  geom_segment(aes(x=ymd_hms("2023-04-11 15:25:00"), xend=ymd_hms("2023-04-11 15:25:00"), y = 0.7, yend = 0.2), arrow = arrow(length = unit(0.5, "cm"))) +
  #geom_segment(aes(x=ymd_hms("2023-04-11 15:25:00"), xend=ymd_hms("2023-04-11 15:25:00"), y = -0.2, yend = -0.9), arrow = arrow(length = unit(0.5, "cm"))) +
  labs(x="Date and Time", y="pH difference", color = "") +
  
  annotate("text", y=0, x=ymd_hms("2023-04-11 16:45:00"), label="Mean = 0.89") +
  geom_segment(aes(x=ymd_hms("2023-04-11 16:45:00"), xend=ymd_hms("2023-04-11 16:45:00"), y = 0.2, yend = 0.7), arrow = arrow(length = unit(0.5, "cm"))) +
  geom_segment(aes(x=ymd_hms("2023-04-11 16:45:00"), xend=ymd_hms("2023-04-11 16:45:00"), y = -0.2, yend = -0.7), arrow = arrow(length = unit(0.5, "cm"))) +
  labs(x="Date and Time", y="Temperature difference (C)", color = "") +
  
  scale_x_datetime(breaks = scales::date_breaks("30 min"), 
                   labels = date_format("%d %b %Y %H:%M")) +
  #scale_color_manual(values=c("#D55E00", "#0072B2","#56B4E9"),labels = c("New Design", "Old Design", "Old Design"), guide = guide_legend(reverse = TRUE)) +  
  theme_bw() +
  theme(axis.text.x=element_text(angle=20, vjust = 1, hjust=1),
        legend.position = "top")

ggsave(here("figures", "final", "temp-difference.png"), height=10, width=15, units="cm")
```

## Now do this with raw, voltage data
```{r}
file_names <- list.files(here("data", "CLEAN"), pattern = ".csv", recursive = FALSE, full.names = TRUE)

merged <- read_csv(file_names, col_names = TRUE) %>%
  mutate(date_time = round_date(date_time, "5 seconds"))

ggplot(merged, aes(x=date_time)) +
  geom_point(aes(y=v4, color=logger))
```

Subset for HOT times
```{r}
merged_hot1 <- merged %>%
  filter(date_time > ymd_hms("2023-04-10 15:15:00"), date_time < ymd_hms("2023-04-10 20:00:00"))
merged_hot2 <- merged %>%
  filter(date_time > ymd_hms("2023-04-08 13:00:00"), date_time < ymd_hms("2023-04-08 17:38:00"))
merged_hot3 <- merged %>%
  filter(date_time < ymd_hms("2023-04-07 14:38:00"), date_time > ymd_hms("2023-04-07 11:45:00"))
merged_hot4 <- merged %>%
  filter(date_time>ymd_hms("2023-04-12 16:45:00"))

merged_hot <-merged %>%
  filter(date_time > ymd_hms("2023-04-11 15:00:00"), date_time < ymd_hms("2023-04-11 16:05:00"))

ggplot(merged_hot, aes(x=date_time)) +
  geom_point(aes(y=v4, color=logger))

merged_hot_sd <- merged_hot %>%
  group_by(logger) %>%
  summarize(mean = mean(v4),
            sd = sd(v4))
```

Subset for COLD times
```{r}
merged_cold1 <- merged %>%
  filter(date_time > ymd_hms("2023-04-10 12:15:00"), date_time < ymd_hms("2023-04-10 13:00:00"))
merged_cold2 <- merged %>%
  filter(date_time > ymd_hms("2023-04-09 15:15:00"), date_time < ymd_hms("2023-04-09 17:00:00"))
merged_cold3 <- merged %>%
  filter(date_time>ymd_hms("2023-04-12 13:00:00"), date_time < ymd_hms("2023-04-12 15:20:00"))

merged_cold <- merged %>%
  filter(date_time < ymd_hms("2023-04-09 18:00:00"), date_time > ymd_hms("2023-04-09 15:00:00"))

ggplot(merged_cold, aes(x=date_time)) +
  geom_point(aes(y=v4, color=logger))

merged_cold_sd <- merged_cold %>%
  group_by(logger) %>%
  summarize(mean = mean(v4),
            sd = sd(v4))
```

Subset for room temp (way more stable)
```{r}
merged_room <- merged %>%
  filter(date_time < ymd_hms("2023-04-08 03:00:30"), date_time > ymd_hms("2023-04-08 01:00:00"))

ggplot(merged_room, aes(x=date_time)) +
  geom_point(aes(y=v4, color=logger))

merged_room_sd <- merged_room %>%
  group_by(logger) %>%
  summarize(mean = mean(v4),
            sd = sd(v4))
```

```{r}
#Subset it for the swap time
merged_swap <- merged %>%
    filter(date_time < ymd_hms("2023-04-09 18:00:00"), date_time > ymd_hms("2023-04-09 15:00:00"))  #for ARD vs MAD 4/9
  filter(date_time > ymd_hms("2023-04-11 12:00:00"), date_time < "2023-04-11 20:00:00") %>%
  mutate(logger = ifelse(date_time < ymd_hms("2023-04-11 14:55:00"), "madgetech_comp", logger),
         logger = ifelse(date_time > ymd_hms("2023-04-11 13:45:00") & logger == "madgetech_comp" & durafet == "green", "Madgetech-1",
                         ifelse(date_time > ymd_hms("2023-04-11 13:45:00") & logger == "madgetech_comp" & durafet == "red", "Madgetech-2",
                                ifelse(date_time < ymd_hms("2023-04-11 13:45:00") & logger == "madgetech_comp" & durafet == "green","Madgetech-2",
                                       ifelse(date_time < ymd_hms("2023-04-11 13:45:00") & logger == "madgetech_comp" & durafet == "red","Madgetech-1",logger)))))

merge_swap_diff <- merged_swap %>%
  arrange(date_time) %>%
  group_by(logger) %>%
  mutate(diff_lag = abs(v4-lag(v4, default = first(v4)))) %>%
  filter(#!diff_lag == 0) %>%
         !diff_lag > 0.05) %>% #remove lag values associated with start time
  ungroup()

merged_diff <- merge_swap_diff %>%
  arrange(date_time) %>%
  mutate(period = ifelse(date_time <= ymd_hms("2023-04-09 16:00:00"), 1, 2)) %>% #for ARD vs MAD 4/9 comparison
  #mutate(period = ifelse(date_time<=ymd_hms("2023-04-11 13:45:00"), "1",
  #                       ifelse(date_time<=ymd_hms("2023-04-11 14:54:00") & date_time>=ymd_hms("2023-04-11 13:45:00"), "2",
  #                              ifelse(date_time>=ymd_hms("2023-04-11 14:54:00") & date_time<=ymd_hms("2023-04-11 15:55:00"), "3", "4")))) %>%
  group_by(period) %>%
  mutate(diff_time = date_time-lag(date_time, default = first(date_time)),
         diff_temp = v4-lag(v4, default=first(v4)),
         diff_ph = v1-lag(v1, default=first(v1))) %>%
  filter(!diff_ph == 0) %>%
  ungroup() #%>%
  ## DO BELOW ONLY FOR GRAPHS!!!!!!!!!!!!!!!!!!!!!!!!!!!!!!!!
  #mutate(logger = ifelse(logger == "Madgetech-2", "madgetech", logger)) %>%
  #filter(date_time <= ymd_hms("2023-04-11 14:54:00"))

ggplot(merged_diff, aes(x=date_time)) +
  geom_point(aes(y=v4, color=logger))
```

```{r}
merged_diff_sum <- merged_diff %>%
  group_by(period, logger) %>%
  summarize(mean_temp = mean(v4),
            #sd_temp = sd(v4),
            mean_ph = mean(v1),
            #sd_ph = sd(v1),
            mean_diff_t = mean(diff_temp),
            mean_diff_p = mean(diff_ph))

avg_t_1 <- abs(mean(merged_diff_sum[[1,5]], merged_diff_sum[[2,5]]))
avg_t_2 <- abs(mean(merged_diff_sum[[3,5]], merged_diff_sum[[4,5]]))
avg_t_1 <- abs(mean(merged_diff_sum[[5,5]], merged_diff_sum[[6,5]]))
avg_t_2 <- abs(mean(merged_diff_sum[[7,5]], merged_diff_sum[[8,5]]))
avg_temp <- avg_t_1-avg_t_2

avg_p_1 <- abs(mean(merged_diff_sum[[1,6]], merged_diff_sum[[2,6]]))
avg_p_2 <- abs(mean(merged_diff_sum[[3,6]], merged_diff_sum[[4,6]]))
avg_p_1 <- abs(mean(merged_diff_sum[[5,6]], merged_diff_sum[[6,6]]))
avg_p_2 <- abs(mean(merged_diff_sum[[7,6]], merged_diff_sum[[8,6]]))
avg_ph <- avg_p_2-avg_p_1

period1 <- merged_diff %>%
  filter(period==1)
period2 <- merged_diff %>%
  filter(period==2)
period3 <- merged_diff %>%
  filter(period==3)
period4 <- merged_diff %>%
  filter(period==4)

ggplot(data=merged_diff, aes(x=date_time)) +
  geom_line(data=period1, aes(y=diff_ph, color=logger), size=1) +
  geom_line(data=period2, aes(y=diff_ph, color=logger), size=1) +
  geom_line(data=period3, aes(y=diff_ph, color=logger), size=1) +
  geom_line(data=period4, aes(y=diff_ph, color=logger), size=1) +
  
  annotate("text", y=0, x=ymd_hms("2023-04-11 13:15:00"), label="Mean = 31.65") +
  geom_segment(aes(x=ymd_hms("2023-04-11 13:15:00"), xend=ymd_hms("2023-04-11 13:15:00"), y = 5, yend = 25), arrow = arrow(length = unit(0.5, "cm"))) +
  geom_segment(aes(x=ymd_hms("2023-04-11 13:15:00"), xend=ymd_hms("2023-04-11 13:15:00"), y = -5, yend = -25), arrow = arrow(length = unit(0.5, "cm"))) +
  labs(x="Date and Time", y="pH difference", color = "") +
  
  annotate("text", y=0, x=ymd_hms("2023-04-11 14:15:00"), label="Mean = 32.30") +
  geom_segment(aes(x=ymd_hms("2023-04-11 14:15:00"), xend=ymd_hms("2023-04-11 14:15:00"), y = 5, yend = 25), arrow = arrow(length = unit(0.5, "cm"))) +
  geom_segment(aes(x=ymd_hms("2023-04-11 14:15:00"), xend=ymd_hms("2023-04-11 14:15:00"), y = -5, yend = -25), arrow = arrow(length = unit(0.5, "cm"))) +
  labs(x="Date and Time", y="pH difference", color = "") +
  
  annotate("text", y=0, x=ymd_hms("2023-04-11 15:25:00"), label="Mean = 32.11") +
  geom_segment(aes(x=ymd_hms("2023-04-11 15:25:00"), xend=ymd_hms("2023-04-11 15:25:00"), y = 5, yend = 25), arrow = arrow(length = unit(0.5, "cm"))) +
  geom_segment(aes(x=ymd_hms("2023-04-11 15:25:00"), xend=ymd_hms("2023-04-11 15:25:00"), y = -5, yend = -25), arrow = arrow(length = unit(0.5, "cm"))) +
  labs(x="Date and Time", y="pH difference", color = "") +
  
  annotate("text", y=0, x=ymd_hms("2023-04-11 16:45:00"), label="Mean = 31.93") +
  geom_segment(aes(x=ymd_hms("2023-04-11 16:45:00"), xend=ymd_hms("2023-04-11 16:45:00"), y = 5, yend = 25), arrow = arrow(length = unit(0.5, "cm"))) +
  geom_segment(aes(x=ymd_hms("2023-04-11 16:45:00"), xend=ymd_hms("2023-04-11 16:45:00"), y = -5, yend = -25), arrow = arrow(length = unit(0.5, "cm"))) +
  labs(x="Date and Time", y="mV difference (pH)", color = "") +
  
  scale_x_datetime(breaks = scales::date_breaks("30 min"), 
                   labels = date_format("%d %b %Y %H:%M")) +
  scale_color_manual(values=c("#D55E00", "#0072B2","#56B4E9"),labels = c("New Design", "Old Design", "Old Design"), guide = guide_legend(reverse = TRUE)) +
  theme_bw() +
  theme(axis.text.x=element_text(angle=20, vjust = 1, hjust=1),
        legend.position = "top")

ggsave(here("figures", "final", "ph-difference-mv.png"), height=10, width=15, units="cm")

ggplot(data=merged_diff, aes(x=date_time)) +
  geom_line(data=period1, aes(y=diff_temp, color=logger), size=1) +
  geom_line(data=period2, aes(y=diff_temp, color=logger), size=1) +
  geom_line(data=period3, aes(y=diff_temp, color=logger), size=1) +
  geom_line(data=period4, aes(y=diff_temp, color=logger), size=1) +
  
  annotate("text", y=1.5, x=ymd_hms("2023-04-11 13:15:00"), label="Mean = 0.40") +
  geom_segment(aes(x=ymd_hms("2023-04-11 13:15:00"), xend=ymd_hms("2023-04-11 13:15:00"), y = 1.2, yend = 0.4), arrow = arrow(length = unit(0.5, "cm"))) +
  #geom_segment(aes(x=ymd_hms("2023-04-11 13:15:00"), xend=ymd_hms("2023-04-11 13:15:00"), y = -0.1, yend = -0.3), arrow = arrow(length = unit(0.5, "cm"))) +
  labs(x="Date and Time", y="Temperature difference (C)", color = "") +
  
  annotate("text", y=1.5, x=ymd_hms("2023-04-11 14:15:00"), label="Mean = 0.30") +
  geom_segment(aes(x=ymd_hms("2023-04-11 14:15:00"), xend=ymd_hms("2023-04-11 14:15:00"), y = 1.2, yend = 0.4), arrow = arrow(length = unit(0.5, "cm"))) +
  #geom_segment(aes(x=ymd_hms("2023-04-11 14:15:00"), xend=ymd_hms("2023-04-11 14:15:00"), y = -0.2, yend = -0.9), arrow = arrow(length = unit(0.5, "cm"))) +
  labs(x="Date and Time", y="pH difference", color = "") +
  
  annotate("text", y=0, x=ymd_hms("2023-04-11 15:25:00"), label="Mean = 0.02") +
  geom_segment(aes(x=ymd_hms("2023-04-11 15:25:00"), xend=ymd_hms("2023-04-11 15:25:00"), y = 0.2, yend = 1), arrow = arrow(length = unit(0.5, "cm"))) +
  geom_segment(aes(x=ymd_hms("2023-04-11 15:25:00"), xend=ymd_hms("2023-04-11 15:25:00"), y = -0.2, yend = -1), arrow = arrow(length = unit(0.5, "cm"))) +
  labs(x="Date and Time", y="pH difference", color = "") +
  
  annotate("text", y=0, x=ymd_hms("2023-04-11 16:45:00"), label="Mean = 0.89") +
  geom_segment(aes(x=ymd_hms("2023-04-11 16:45:00"), xend=ymd_hms("2023-04-11 16:45:00"), y = 0.2, yend = 1), arrow = arrow(length = unit(0.5, "cm"))) +
  geom_segment(aes(x=ymd_hms("2023-04-11 16:45:00"), xend=ymd_hms("2023-04-11 16:45:00"), y = -0.2, yend = -1), arrow = arrow(length = unit(0.5, "cm"))) +
  labs(x="Date and Time", y="mV difference (temperature)", color = "") +
  
  scale_x_datetime(breaks = scales::date_breaks("30 min"), 
                   labels = date_format("%d %b %Y %H:%M")) +
  scale_color_manual(values=c("#D55E00", "#0072B2","#56B4E9"),labels = c("New Design", "Old Design", "Old Design"), guide = guide_legend(reverse = TRUE)) +  
  theme_bw() +
  theme(axis.text.x=element_text(angle=20, vjust = 1, hjust=1),
        legend.position = "top")

ggsave(here("figures", "final", "temp-difference-mv.png"), height=10, width=15, units="cm")
```

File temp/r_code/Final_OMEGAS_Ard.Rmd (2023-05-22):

---
title: "Apply GREEN and RED calibration data to Arduino readings"
author: "Amelia Ritger"
date: "2023-04-07"
output: html_document
---

```{r setup, include=FALSE}
knitr::opts_chunk$set(echo = TRUE)
```

##Load libraries, set constants
```{r}
library(tidyverse)
library(readr)
library(janitor)
library(here)
library(lubridate)

#Tris calibration values
filename_red_tris <-  "red_mad_25_omegas_calib"
filename_green_tris <- "green_ard_25_omegas_calib" 

filename_ard_green <- "green_ard_5.2"  #5.1, 5.2, 10, 20, 25, 25.2
filename_ard_red <- "red_ard_5" #5,10,20,25,25.2
temperature <- "5"

#apply temperature correction equations to each durafet
temp_corr_green_m <- 0.0347 #1.995
temp_corr_green_b <- 0.679 #1.995
temp_corr_red_m <- 0.0775 #1.949
temp_corr_red_b <- 0.543 #1.949

#calculated uncertainties using raw data
var_ard <- 0 #calculated uncertainties using raw data
var_ard_real <- 0 #calculated uncertainties using raw data
var_madg <- 0 #calculated uncertainties using raw data
#var_ard <- 0.82869
#var_ard_real <- 0.16565
#var_madg <- 0.16978

#ard_correction_m <- 1+0.099 #slope coefficient for arduino (corrected with HOBO)
#ard_correction_b <- -0.632
#madg_correction_m <- 1+0.106 #slope coefficient for madgetech (corrected with HOBO)
#madg_correction_b <- 0.123

#OLD VALUES: (what happened??)
# ard_correction_m <- 1+0.229 #slope coefficient for arduino (corrected with HOBO)
# ard_correction_b <- 1+0.475
# madg_correction_m <- 1+0.202 #slope coefficient for madgetech (corrected with HOBO)
# madg_correction_b <- 1+1.02

 madg_correction_m <- 1 #slope coefficient for madgetech (corrected with HOBO)
 madg_correction_b <- 0
 ard_correction_m <- 1 #slope coefficient for arduino (corrected with HOBO)
 ard_correction_b <- 0
```

## Run "Ideal" calibration for Arduino GREEN deployment data
```{r}
#load calibration data
calibration_values <- read_csv(here("data", "calibrated", paste(filename_green_tris,".csv",sep=""))) # read in tris data excel file

rawdata_all <- read_csv(here("data", "raw", "april-green", paste(filename_ard_green,".csv",sep=""))) %>% # read in tris data excel file
  #mutate("J4" = rawdata_all[12]-rawdata_all[18]) %>%
  clean_names() %>% # read in tris data excel file
  mutate(date_lubridate=mdy(date)) %>% # tell R "date" is a DATE
  mutate(time_lubridate=hms(time)) %>% # tell R "time" is a TIME
  unite(date_time, c(date, time), sep = " ", remove = TRUE) %>% # combine the date and time columns
  mutate(date_time_lubridate=mdy_hms(date_time)) %>%# tell R "date_time" is a DATE and a TIME
  mutate(j4 = j4_oversampled_mean_m_v - j4_oversampled_mean_m_v_2)

rawdata <- rawdata_all %>%
  select(24, 3,8,9,25) %>%
  setNames(c("date_time", "v1", "v3", "v2", "v4")) %>%
  mutate(v2 = abs(v2))
  
raw_voltages <- data.frame(rawdata$v1,rawdata$v2,rawdata$v3,rawdata$v4) %>% # create OMEGAS data frame with the raw voltages
  mutate(mv1=as.numeric(rawdata.v1),
         mv2=as.numeric(rawdata.v2),
         mv3=as.numeric(rawdata.v3),
         mv4=as.numeric(rawdata.v4)) %>% # changing data to numeric arguments
  select(mv1, mv2, mv3, mv4) # cleaning data frame

omegas_temp_raw <- raw_voltages %>% # create OMEGAS data frame with the raw voltages
  mutate(v1=(mv1/1000),
         v2=(mv2/1000),
         v3=(mv3/1000),
         v4=(mv4/1000)) %>% # converting the mV to volts
  mutate(vbattery=((v2/100)*101.57)) %>% # calculate vbattery
  mutate(z=(v4/100)+vbattery*((15000*1)/((1000000*1)+(15000*1)))) %>% # calculate column k
  mutate(y=(z*(1000000*1))) %>% # calculate column l
  mutate(rthermistor=(y/(vbattery-z))) %>% # calculate Rthermistor
  mutate(sh_a=as.numeric(0.00106329736674527)) %>% # create column with Steinhart constant A
  mutate(sh_b=as.numeric(0.000251377462346306)) %>% # create column with Steinhart constant B
  mutate(sh_c=as.numeric(2.55455247726963E-08)) %>% # create column with Steinhart constant C
  mutate(k=(1/(sh_a+sh_b*log(rthermistor)+sh_c*(log(rthermistor))^3))) %>% # create column to calculate intermediate value K
  mutate(durafet=as.numeric((k-273.15))) %>% # create new column to calculate durafet therm
  mutate(durafet=(durafet*temp_corr_green_m)+temp_corr_green_b) %>% # do temperature correction
  mutate(durafet=((durafet*ard_correction_m)-ard_correction_b)) %>% #do temperature correction
  mutate(durafet=(durafet+var_ard)) #correct with calculated uncertainties

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

raw_tris_ph <- data.frame(temp,b,c,d,e,f,g,h,i,j,t,k,m) %>% # create tris pH template as a data frame with all above columns
  mutate(n=(b-(c*m)-(d*m*m))*1/t) %>% # create column n
  mutate(o=(-e+(f*m)+(g*m*m))) %>% # create column o
  mutate(p=(h-(i*m))*log(t)-(j*(t))) %>% # create column p
  mutate(trisph=(n+o+p)) # calculate tris pH, add as a new column to tris pH template data frame

omegas_ph_raw <- data.frame(rawdata$date_time,omegas_temp_raw$durafet,omegas_temp_raw$v1) %>%
   # create data frame with durafet therm and voltage 1 values
  rename(date_time=rawdata.date_time,
         durafet_temp=omegas_temp_raw.durafet,
         v1=omegas_temp_raw.v1) %>% # rename date/time column from trisdata data frame
  mutate(trisph=raw_tris_ph$trisph) %>% # add tris pH values into calibration dataframe TRIS PH IS NOT THE SAME LENGTH AS THE RAW DATA
  mutate(tk=omegas_temp_raw$durafet+273.15) %>% # add TK column to data frame
  mutate(st=(8.31451*tk/96487*log(10))) %>% # add S(T) column to data frame
  mutate(eo=((calibration_values$v1)-(calibration_values$trisph)*8.31451*(273.15+calibration_values$durafet_temp)*log(10)/96487)) %>% # calculate eo value using calibration values
  mutate(eot=(eo-(0.001*(tk-(273.15+calibration_values$durafet_temp))))) %>% # add Eo(T) column to data frame
  mutate(omegasrawph=(omegas_temp_raw$v1-eot)/st) %>% # add pH column to data frame
  mutate(diff=(trisph-omegasrawph)) # add difference column (tris pH - omegas pH) to data frame

raw_calibrated <- omegas_ph_raw %>% # create new dataframe using omegasph_raw data
  select(date_time, durafet_temp, omegasrawph) %>% # keep only date/time, temperature, and pH columns
  rename("p_h"=3)

#unique identifier for final calibrated data
raw_calibrated_ideal <- raw_calibrated %>%
  mutate(logger = "arduino",
         tolerance = "ideal",
         temperature = temperature,
         durafet = "green")

#Write .csv
write.csv(raw_calibrated_ideal, here("data", "calibrated", paste(filename_ard_green,"_omegas.csv", sep="")),row.names = FALSE) # create csv with calibrated values
```

## Run "Ideal" calibration for Arduino RED deployment data
```{r}
#load calibration data
calibration_values <- read_csv(here("data", "calibrated", paste(filename_red_tris,".csv",sep=""))) # read in tris data excel file

rawdata_all <- read_csv(here("data", "raw", "april-red", paste(filename_ard_red,".csv",sep=""))) %>% # read in tris data excel file
  clean_names() %>% # read in tris data excel file
  mutate(date_lubridate=mdy(date)) %>% # tell R "date" is a DATE
  mutate(time_lubridate=hms(time)) %>% # tell R "time" is a TIME
  unite(date_time, c(date, time), sep = " ", remove = TRUE) %>% # combine the date and time columns
  mutate(date_time_lubridate=mdy_hms(date_time)) %>%# tell R "date_time" is a DATE and a TIME
  mutate(j4 = j4_oversampled_mean_m_v - j4_oversampled_mean_m_v_2)

rawdata <- rawdata_all %>%
  select(24, 3,8,9,25) %>%
  setNames(c("date_time", "v1", "v3", "v2", "v4")) %>%
  mutate(v2 = abs(v2))
  
raw_voltages <- data.frame(rawdata$v1,rawdata$v2,rawdata$v3,rawdata$v4) %>% # create OMEGAS data frame with the raw voltages
  mutate(mv1=as.numeric(rawdata.v1),
         mv2=as.numeric(rawdata.v2),
         mv3=as.numeric(rawdata.v3),
         mv4=as.numeric(rawdata.v4)) %>% # changing data to numeric arguments
  select(mv1, mv2, mv3, mv4) # cleaning data frame

omegas_temp_raw <- raw_voltages %>% # create OMEGAS data frame with the raw voltages
  mutate(v1=(mv1/1000),
         v2=(mv2/1000),
         v3=(mv3/1000),
         v4=(mv4/1000)) %>% # converting the mV to volts
  mutate(vbattery=((v2/100)*101.57)) %>% # calculate vbattery
  mutate(z=(v4/100)+vbattery*((15000*1)/((1000000*1)+(15000*1)))) %>% # calculate column k
  mutate(y=(z*(1000000*1))) %>% # calculate column l
  mutate(rthermistor=(y/(vbattery-z))) %>% # calculate Rthermistor
  mutate(sh_a=as.numeric(0.00106329736674527)) %>% # create column with Steinhart constant A
  mutate(sh_b=as.numeric(0.000251377462346306)) %>% # create column with Steinhart constant B
  mutate(sh_c=as.numeric(2.55455247726963E-08)) %>% # create column with Steinhart constant C
  mutate(k=(1/(sh_a+sh_b*log(rthermistor)+sh_c*(log(rthermistor))^3))) %>% # create column to calculate intermediate value K
  mutate(durafet=as.numeric((k-273.15))) %>% # create new column to calculate durafet therm
  mutate(durafet=(durafet*temp_corr_red_m)+temp_corr_red_b) %>% # do temperature correction
  mutate(durafet=((durafet*ard_correction_m)-ard_correction_b)) %>% #do temperature correction
  mutate(durafet=(durafet+var_ard)) #correct with calculated uncertainties

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

raw_tris_ph <- data.frame(temp,b,c,d,e,f,g,h,i,j,t,k,m) %>% # create tris pH template as a data frame with all above columns
  mutate(n=(b-(c*m)-(d*m*m))*1/t) %>% # create column n
  mutate(o=(-e+(f*m)+(g*m*m))) %>% # create column o
  mutate(p=(h-(i*m))*log(t)-(j*(t))) %>% # create column p
  mutate(trisph=(n+o+p)) # calculate tris pH, add as a new column to tris pH template data frame

omegas_ph_raw <- data.frame(rawdata$date_time,omegas_temp_raw$durafet,omegas_temp_raw$v1) %>%
   # create data frame with durafet therm and voltage 1 values
  rename(date_time=rawdata.date_time,
         durafet_temp=omegas_temp_raw.durafet,
         v1=omegas_temp_raw.v1) %>% # rename date/time column from trisdata data frame
  mutate(trisph=raw_tris_ph$trisph) %>% # add tris pH values into calibration dataframe TRIS PH IS NOT THE SAME LENGTH AS THE RAW DATA
  mutate(tk=omegas_temp_raw$durafet+273.15) %>% # add TK column to data frame
  mutate(st=(8.31451*tk/96487*log(10))) %>% # add S(T) column to data frame
  mutate(eo=((calibration_values$v1)-(calibration_values$trisph)*8.31451*(273.15+calibration_values$durafet_temp)*log(10)/96487)) %>% # calculate eo value using calibration values
  mutate(eot=(eo-(0.001*(tk-(273.15+calibration_values$durafet_temp))))) %>% # add Eo(T) column to data frame
  mutate(omegasrawph=(omegas_temp_raw$v1-eot)/st) %>% # add pH column to data frame
  mutate(diff=(trisph-omegasrawph)) # add difference column (tris pH - omegas pH) to data frame

raw_calibrated <- omegas_ph_raw %>% # create new dataframe using omegasph_raw data
  select(date_time, durafet_temp, omegasrawph) %>% # keep only date/time, temperature, and pH columns
  rename("p_h"=3)

#unique identifier for final calibrated data
raw_calibrated_ideal <- raw_calibrated %>%
  mutate(logger = "arduino",
         tolerance = "ideal",
         temperature = temperature,
         durafet = "red")

#Write .csv
write.csv(raw_calibrated_ideal, here("data", "calibrated", paste(filename_ard_red,"_omegas.csv", sep="")),row.names = FALSE) # create csv with calibrated values
```

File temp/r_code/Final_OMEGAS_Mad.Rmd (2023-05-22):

---
title: "Apply GREEN and RED calibration data to Madgetech readings"
author: "Amelia Ritger"
date: "2023-04-07"
output: html_document
---

```{r setup, include=FALSE}
knitr::opts_chunk$set(echo = TRUE)
```

##Load libraries, set constants
```{r}
library(tidyverse)
library(readr)
library(janitor)
library(here)
library(lubridate)

#Tris calibration values
filename_red_tris <-  "red_mad_25_omegas_calib"
filename_green_tris <- "green_ard_25_omegas_calib"

filename_mad_green <- "green_mad_25.2"
filename_mad_red <- "red_mad_25.2" #5.1, 5.2, 10, 20, 25, 25.2
temperature <- "25.2"

#apply temperature correction equations
temp_corr_green_m <- 0.0347 #1.995
temp_corr_green_b <- 0.679 #1.995
temp_corr_red_m <- 0.0775 #1.949
temp_corr_red_b <- 0.543 #1.949

#calculated uncertainties using raw data
var_ard <- 0 #calculated uncertainties using raw data
var_ard_real <- 0 #calculated uncertainties using raw data
var_madg <- 0 #calculated uncertainties using raw data
#var_ard <- 0.82869
#var_ard_real <- 0.16565
#var_madg <- 0.16978

#ard_correction_m <- 1+0.099 #slope coefficient for arduino (corrected with HOBO)
#ard_correction_b <- -0.632
#madg_correction_m <- 1+0.106 #slope coefficient for madgetech (corrected with HOBO)
#madg_correction_b <- 0.123

#OLD VALUES: (what happened??)
# ard_correction_m <- 1+0.229 #slope coefficient for arduino (corrected with HOBO)
# ard_correction_b <- 1+0.475
# madg_correction_m <- 1+0.202 #slope coefficient for madgetech (corrected with HOBO)
# madg_correction_b <- 1+1.02

 madg_correction_m <- 1 #slope coefficient for madgetech (corrected with HOBO)
 madg_correction_b <- 0
 ard_correction_m <- 1 #slope coefficient for arduino (corrected with HOBO)
 ard_correction_b <- 0
```

## Run "Ideal" calibration for Madgetech GREEN deployment data
```{r}
#load calibration data
calibration_values <- read_csv(here("data", "calibrated", paste(filename_green_tris,".csv",sep=""))) # read in tris data excel file

rawdata_all <- read_csv(here("data", "raw", "april-green", paste(filename_mad_green,".csv",sep=""))) %>% # read in tris data excel file
  filter(row_number()!=c(1:5)) %>% # remove the first 5 rows
  row_to_names(row_number=1) %>% # make the top row the column headers
  rename("Date"=1,
         "Time"=2) %>% # rename date and time columns
  clean_names() %>% # read in tris data excel file
  mutate(date_lubridate=mdy(date)) %>% # tell R "date" is a DATE
  mutate(time_lubridate=hms(time)) %>% # tell R "time" is a TIME
  unite(date_time, c(date, time), sep = " ", remove = TRUE) %>% # combine the date and time columns
  mutate(date_time_lubridate=mdy_hms(date_time)) # tell R "date_time" is a DATE and a TIME

rawdata <- rawdata_all %>%
  select(8, 2:5) %>%
  setNames(c("date_time", "v1", "v2", "v3", "v4"))
  
raw_voltages <- data.frame(rawdata$v1,rawdata$v2,rawdata$v3,rawdata$v4) %>% # create OMEGAS data frame with the raw voltages
  mutate(mv1=as.numeric(rawdata.v1),
         mv2=as.numeric(rawdata.v2),
         mv3=as.numeric(rawdata.v3),
         mv4=as.numeric(rawdata.v4)) %>% # changing data to numeric arguments
  select(mv1, mv2, mv3, mv4) # cleaning data frame

omegas_temp_raw <- raw_voltages %>% # create OMEGAS data frame with the raw voltages
  mutate(v1=(mv1/1000),
         v2=(mv2/1000),
         v3=(mv3/1000),
         v4=(mv4/1000)) %>% # converting the mV to volts
  mutate(vbattery=((v2/100)*101.57)) %>% # calculate vbattery
  mutate(z=(v4/100)+vbattery*((15000*1)/((1000000*1)+(15000*1)))) %>% # calculate column k
  mutate(y=(z*(1000000*1))) %>% # calculate column l
  mutate(rthermistor=(y/(vbattery-z))) %>% # calculate Rthermistor
  mutate(sh_a=as.numeric(0.00106329736674527)) %>% # create column with Steinhart constant A
  mutate(sh_b=as.numeric(0.000251377462346306)) %>% # create column with Steinhart constant B
  mutate(sh_c=as.numeric(2.55455247726963E-08)) %>% # create column with Steinhart constant C
  mutate(k=(1/(sh_a+sh_b*log(rthermistor)+sh_c*(log(rthermistor))^3))) %>% # create column to calculate intermediate value K
  mutate(durafet=as.numeric((k-273.15))) %>% # create new column to calculate durafet therm
  mutate(durafet=(durafet*temp_corr_green_m)+temp_corr_green_b) %>% # do temperature correction
  mutate(durafet=((durafet*madg_correction_m)-madg_correction_b)) %>% #do temperature correction
  mutate(durafet=(durafet+var_madg)) #correct with calculated uncertainties

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

raw_tris_ph <- data.frame(temp,b,c,d,e,f,g,h,i,j,t,k,m) %>% # create tris pH template as a data frame with all above columns
  mutate(n=(b-(c*m)-(d*m*m))*1/t) %>% # create column n
  mutate(o=(-e+(f*m)+(g*m*m))) %>% # create column o
  mutate(p=(h-(i*m))*log(t)-(j*(t))) %>% # create column p
  mutate(trisph=(n+o+p)) # calculate tris pH, add as a new column to tris pH template data frame

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

raw_calibrated <- omegas_ph_raw %>% # create new dataframe using omegasph_raw data
  select(date_time, durafet_temp, omegasrawph) %>% # keep only date/time, temperature, and pH columns
  rename("p_h"=3)

#unique identifier for final calibrated data
calibration_values <- raw_calibrated %>%
  mutate(logger = "madgetech",
         tolerance = "ideal",
         temperature = temperature,
         durafet = "green")

#Write .csv
write.csv(calibration_values, here("data", "calibrated", paste(filename_mad_green,"_omegas.csv", sep="")),row.names = FALSE) # create csv with calibrated values
```

## Run "Ideal" calibration for Madgetech RED deployment data
```{r}
#load calibration data
calibration_values <- read_csv(here("data", "calibrated", paste(filename_red_tris,".csv",sep=""))) # read in tris data excel file

rawdata_all <- read_csv(here("data", "raw", "april-red", paste(filename_mad_red,".csv",sep=""))) %>% # read in tris data excel file
  filter(row_number()!=c(1:5)) %>% # remove the first 5 rows
  row_to_names(row_number=1) %>% # make the top row the column headers
  rename("Date"=1,
         "Time"=2) %>% # rename date and time columns
  clean_names() %>% # read in tris data excel file
  mutate(date_lubridate=mdy(date)) %>% # tell R "date" is a DATE
  mutate(time_lubridate=hms(time)) %>% # tell R "time" is a TIME
  unite(date_time, c(date, time), sep = " ", remove = TRUE) %>% # combine the date and time columns
  mutate(date_time_lubridate=mdy_hms(date_time)) # tell R "date_time" is a DATE and a TIME

rawdata <- rawdata_all %>%
  select(8, 2:5) %>%
  setNames(c("date_time", "v1", "v2", "v3", "v4"))
  
raw_voltages <- data.frame(rawdata$v1,rawdata$v2,rawdata$v3,rawdata$v4) %>% # create OMEGAS data frame with the raw voltages
  mutate(mv1=as.numeric(rawdata.v1),
         mv2=as.numeric(rawdata.v2),
         mv3=as.numeric(rawdata.v3),
         mv4=as.numeric(rawdata.v4)) %>% # changing data to numeric arguments
  select(mv1, mv2, mv3, mv4) # cleaning data frame

omegas_temp_raw <- raw_voltages %>% # create OMEGAS data frame with the raw voltages
  mutate(v1=(mv1/1000),
         v2=(mv2/1000),
         v3=(mv3/1000),
         v4=(mv4/1000)) %>% # converting the mV to volts
  mutate(vbattery=((v2/100)*101.57)) %>% # calculate vbattery
  mutate(z=(v4/100)+vbattery*((15000*1)/((1000000*1)+(15000*1)))) %>% # calculate column k
  mutate(y=(z*(1000000*1))) %>% # calculate column l
  mutate(rthermistor=(y/(vbattery-z))) %>% # calculate Rthermistor
  mutate(sh_a=as.numeric(0.00106329736674527)) %>% # create column with Steinhart constant A
  mutate(sh_b=as.numeric(0.000251377462346306)) %>% # create column with Steinhart constant B
  mutate(sh_c=as.numeric(2.55455247726963E-08)) %>% # create column with Steinhart constant C
  mutate(k=(1/(sh_a+sh_b*log(rthermistor)+sh_c*(log(rthermistor))^3))) %>% # create column to calculate intermediate value K
  mutate(durafet=as.numeric((k-273.15))) %>% # create new column to calculate durafet therm
  mutate(durafet=(durafet*temp_corr_green_m)+temp_corr_green_b) %>% # do temperature correction
  mutate(durafet=((durafet*madg_correction_m)-madg_correction_b)) %>% #do temperature correction
  mutate(durafet=(durafet+var_madg)) #correct with calculated uncertainties

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

raw_tris_ph <- data.frame(temp,b,c,d,e,f,g,h,i,j,t,k,m) %>% # create tris pH template as a data frame with all above columns
  mutate(n=(b-(c*m)-(d*m*m))*1/t) %>% # create column n
  mutate(o=(-e+(f*m)+(g*m*m))) %>% # create column o
  mutate(p=(h-(i*m))*log(t)-(j*(t))) %>% # create column p
  mutate(trisph=(n+o+p)) # calculate tris pH, add as a new column to tris pH template data frame

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

raw_calibrated <- omegas_ph_raw %>% # create new dataframe using omegasph_raw data
  select(date_time, durafet_temp, omegasrawph) %>% # keep only date/time, temperature, and pH columns
  rename("p_h"=3)

#unique identifier for final calibrated data
calibration_values <- raw_calibrated %>%
  mutate(logger = "madgetech",
         tolerance = "ideal",
         temperature = temperature,
         durafet = "red")

#Write .csv
write.csv(calibration_values, here("data", "calibrated", paste(filename_mad_red,"_omegas.csv", sep="")),row.names = FALSE) # create csv with calibrated values
```

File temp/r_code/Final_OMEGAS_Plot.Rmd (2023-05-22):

---
title: "Plot OMEGAS calibrated data"
author: "Amelia Ritger"
date: "2023-04-07"
output: html_document
---

```{r setup, include=FALSE}
knitr::opts_chunk$set(echo = TRUE)
```

##Load libraries, set constants
```{r}
library(tidyverse)
library(readr)
library(janitor)
library(here)
library(lubridate)

pattern_ignore = "calib" #ignore calibration value files
file_names <- list.files(here("data", "calibrated"), pattern = "*.csv", recursive = FALSE, full.names = TRUE)
file_ignore <- list.files(here("data", "calibrated"), pattern = pattern_ignore, recursive = FALSE, full.names = TRUE)
file_names <- setdiff(file_names, file_ignore)

merged <- read_csv(file_names, col_names = TRUE) #%>% filter(date_time > ymd_hms("2022-12-15 16:00:00" ))

merged25 <- merged %>%
  #filter(date_time < ymd_hms("2023-04-07 16:00:00")) %>%
  #filter(date_time > ymd_hms("2023-04-07 15:00:00"))
  filter(date_time < ymd_hms("2023-04-07 14:30:00")) #%>%
  #filter(date_time > ymd_hms("2023-04-07 13:00:00"))

ggplot(merged, aes(x=date_time, y=durafet_temp, group=logger)) +
  geom_point(aes(color=durafet))

ggsave(here("data", "calibrated", "plot_corr.png"))

merged25 <- merged25 %>%
  mutate(real_temp = 25,
         temp_diff = real_temp - durafet_temp) %>%
  group_by(logger) %>%
  summarize(avg_temp_diff = mean(temp_diff))
```

Quick visualize
```{r}
merged_ribbon <- merged %>%
  filter(!logger=="real-arduino") %>%
  mutate(tolerance = ifelse(tolerance %in% c("+5", "+1"), "plus", ifelse(tolerance %in% c("-5", "-1"), "minus", "ideal"))) %>%
  group_by(logger) %>%
  pivot_wider(names_from = tolerance, values_from = c(durafet_temp, p_h))

#plot up temp data
ggplot(data=merged_ribbon, aes(x=date_time)) +
  #geom_point(aes(y=p_h, color=tolerance, shape=logger))
  geom_line(aes(y=durafet_temp_ideal, color=logger)) +
  #geom_line(aes(y=durafet_temp_ideal, color=logger)) +
  geom_ribbon(aes(ymin=durafet_temp_minus, ymax=durafet_temp_plus, fill=logger), alpha=0.2) +
  labs(x="Date and Time", y="Temp (C)") +
  scale_x_datetime(breaks = scales::date_breaks("3 hour"), 
                   labels = date_format("%Y-%m-%d %H:00"),
                   #limits = as.POSIXct(c("2022-12-15 23:00:00","2022-12-16 14:00:00")),
                   expand = c(0, 0)) +
  scale_color_brewer(palette="Set1", direction=-1) +
  scale_fill_brewer(palette="Set1", direction=-1) +
  theme_bw() +
  theme(axis.text.x=element_text(angle=20, vjust = 1, hjust=1),
        legend.position = "top")

ggsave(here("figures", "final", "deployment-temp.png"), height=10, width=15, units="cm")

#plot up pH data
ggplot(data=merged_ribbon, aes(x=date_time)) +
  #geom_point(aes(y=p_h, color=tolerance, shape=logger))
  geom_line(aes(y=p_h_ideal, color=logger)) +
  geom_ribbon(aes(ymin=p_h_minus, ymax=p_h_plus, fill=logger), alpha=0.2) +
  labs(x="Date and Time", y="pH") +
  scale_x_datetime(breaks = scales::date_breaks("3 hour"), 
                   labels = date_format("%Y-%m-%d %H:00"),
                   #limits = as.POSIXct(c("2022-12-15 23:00:00","2022-12-16 14:00:00")),
                   expand = c(0, 0)) +
  scale_color_brewer(palette="Set1", direction=-1) +
  scale_fill_brewer(palette="Set1", direction=-1) +
  theme_bw() +
  theme(axis.text.x=element_text(angle=20, vjust = 1, hjust=1),
        legend.position = "top")

ggsave(here("figures", "final", "deployment-pH.png"), height=10, width=15, units="cm")

#summary stats
merged_sum <- merged_ribbon %>%
  group_by(logger) %>%
  summarize(meant = mean(durafet_temp_ideal),
            sdt = sd(durafet_temp_ideal),
            meanp = mean(p_h_ideal),
            sdp = sd(p_h_ideal))
```

Calculate difference between sensors during field deployments
```{r}
merged_diff <- merged %>%
  #mutate(Logger=ifelse(logger=="arduino", "New design", "Old design")) %>%
  filter(!logger=="real-arduino",
         tolerance=="ideal") %>%
  mutate(date_time = if_else(logger=="arduino" & date_time<ymd_hms("2022-12-15 19:15:44"), date_time+seconds(29), date_time)) %>%
  arrange(date_time) %>%
  mutate(diff_time = date_time-lag(date_time, default = first(date_time)),
         diff_temp = durafet_temp-lag(durafet_temp, default=first(durafet_temp)),
         diff_ph = p_h-lag(p_h, default=first(p_h))) %>%
  ungroup() %>%
  filter(!diff_temp==0) %>%
  mutate(same = ifelse(logger == lag(logger), "YES", "NO"))

merged_diff_sum <- merged_diff %>%
  group_by(logger) %>%
  summarize(mean_temp = abs(mean(diff_temp)),
            mean_ph = abs(mean(diff_ph))) %>%
  summarize(meant = mean(mean_temp),
            meanp = mean(mean_ph))

avg1 <- mean(0.06368266,0.06718390) #get these numbers from above
avg_temp <- avg2-avg1 #0.0401972 -> #0.0438596

avg3 <- mean(0.2478512,0.2479062)
avg4 <- mean(0.2840733,0.2841385) #get these numbers from above
avg_ph <- avg4-avg3 #0.036221 -> 0.036221

```

Load and merge hobo logger data
```{r}
temp <- read_csv(here("data", "temp", paste(pattern_keep,"_hobo_depl.csv", sep="")), col_names = TRUE) %>%
  select(2:3) %>%
  setNames(c("date_time", "hobo_temp")) %>%
  mutate(date_time=mdy_hms(date_time)) #aapply lubridate to date/time column
         #date=format(date_time, '%m/%d/%Y'), #create only date column
         #time=format(date_time, '%H:%M:%S')) #create only time column

merged_all <- full_join(merged, temp)
```

Change sampling range (12/15 - air bubbles for first 8 hours?)
```{r}
merged_sub <- merged %>%
  arrange(date_time) %>%
  filter(date_time >= ymd_hms(filter_time))
```

Plot up Arduino data comparison
```{r}
merged_ribbon <- merged_sub %>%
  filter(!is.na(logger)) %>%
  mutate(tolerance = ifelse(tolerance %in% c("+5", "+1"), "plus", ifelse(tolerance %in% c("-5", "-1"), "minus", "ideal"))) %>%
  mutate(Logger=ifelse(logger=="arduino", "New design", "Old design")) %>%
  select(1:6) %>%
  pivot_wider(names_from = tolerance, values_from = c(durafet_temp, p_h))

#plot up temp data
ggplot(data=merged_ribbon, aes(x=date_time, group=Logger)) +
  #geom_point(aes(y=p_h, color=tolerance, shape=logger))
  geom_line(aes(y=durafet_temp_ideal, color=Logger)) +
  geom_ribbon(aes(ymin=durafet_temp_minus, ymax=durafet_temp_plus, fill=Logger), alpha=0.2) +
  labs(x="Date and Time", y="Temp (C)") +
  scale_x_datetime(breaks = scales::date_breaks("3 hour"), 
                   labels = date_format("%Y-%m-%d %H:00"),
                   #limits = as.POSIXct(c("2022-12-15 23:00:00","2022-12-16 14:00:00")),
                   expand = c(0, 0)) +
  scale_color_brewer(palette="Set1", direction=-1) +
  scale_fill_brewer(palette="Set1", direction=-1) +
  theme_bw() +
  theme(axis.text.x=element_text(angle=20, vjust = 1, hjust=1),
        legend.position = "top")

ggsave(here("figures", "deployment-temp_subset.png"), height=10, width=15, units="cm")

#plot up pH data
ggplot(data=merged_ribbon, aes(x=date_time, group=Logger)) +
  #geom_point(aes(y=p_h, color=tolerance, shape=logger))
  geom_line(aes(y=p_h_ideal, color=Logger)) +
  geom_ribbon(aes(ymin=p_h_minus, ymax=p_h_plus, fill=Logger), alpha=0.2) +
  labs(x="Date and Time", y="pH") +
  scale_x_datetime(breaks = scales::date_breaks("3 hour"), 
                   labels = date_format("%Y-%m-%d %H:00"),
                   #limits = as.POSIXct(c("2022-12-15 23:00:00","2022-12-16 14:00:00")),
                   expand = c(0, 0)) +
  scale_color_brewer(palette="Set1", direction=-1) +
  scale_fill_brewer(palette="Set1", direction=-1) +
  theme_bw() +
  theme(axis.text.x=element_text(angle=20, vjust = 1, hjust=1),
        legend.position = "top")

ggsave(here("figures", "deployment-ph_subset.png"), height=10, width=15, units="cm")

#look at average difference between madgetech and arduino readings for temp and pH
merged_ribbon_compare <- merged_ribbon %>%
  arrange(date_time) %>%
  mutate(diff_temp = durafet_temp_ideal-lag(durafet_temp_ideal, default=first(durafet_temp_ideal)),
         diff_ph = p_h_ideal-lag(p_h_ideal, default=first(p_h_ideal))) %>%
  slice(2:n()) %>%
  group_by(logger) %>%
  summarize(mean_temp_diff = mean(diff_temp),
            sd_temp_diff = sd(diff_temp),
            mean_ph_diff = mean(diff_ph),
            sd_ph_diff = sd(diff_ph))
```

Plot temperature section to compare between HOBO and sensors
```{r}
library(ggpmisc)

merged_comp <- merged_all %>%
   filter(date_time > ymd_hms(start_time),
          date_time < ymd_hms(end_time)) %>%
  filter(tolerance=="ideal" | is.na(tolerance)) %>%
  mutate(logger = ifelse(is.na(logger), "hobo", logger),
         temp_c = ifelse(logger=="hobo", hobo_temp, durafet_temp))

ggplot(data=merged_comp, aes(x=date_time, y=temp_c, group=logger)) +
  #geom_point(aes(y=p_h, color=tolerance, shape=logger))
  geom_point() +
  stat_poly_line() +
  stat_poly_eq(aes(label = paste(after_stat(eq.label)))) +
  scale_y_continuous(limits=c(7.0, 8.8))

ggsave("temp_correction_deploy.png")
```

Get average difference to plot points at different temperatures
```{r}
merge_hobo <- merged_sub %>%
  filter(date_time > ymd_hms(start_time),
          date_time < ymd_hms(end_time)) %>%
  filter(tolerance=="ideal" | is.na(tolerance)) %>%
  arrange(date_time) %>%
  mutate(diff = date_time-lag(date_time, default = first(date_time))) %>%
  mutate(temp_down = hobo_temp,
         temp_up = hobo_temp) %>%
  fill(temp_down, .direction = "down") %>%
  fill(temp_up, .direction = "up") %>%
  mutate(hobo_real = ifelse(diff<20,temp_up,temp_down),
         durafet_fill = ifelse(is.na(hobo_temp),durafet_temp, hobo_real)) %>%
  filter(!is.na(logger)) %>%
  mutate(temp_diff = hobo_real - durafet_temp) %>%
  group_by(logger) %>%
  summarize(mean_diff = mean(temp_diff),
            mean_temp = mean(durafet_fill))

hobo_comp_deploy <- merge_hobo
```

Get average difference between arduino and madgetech to plot difference across temperature
```{r}
merge_comp <- merged %>%
  filter(tolerance=="ideal" | is.na(tolerance)) %>%
  arrange(date_time) %>%
  mutate(diff_time = date_time-lag(date_time, default = first(date_time)),
         diff_temp = durafet_temp-lag(durafet_temp, default=first(durafet_temp))) %>%
  filter(diff_temp > 0.01 | diff_temp < -0.01) %>%
  mutate(diff_time = date_time-lag(date_time, default = first(date_time)),
         diff_temp = durafet_temp-lag(durafet_temp, default=first(durafet_temp))) %>%
    slice(2:n()) %>%
  filter(logger=="arduino") %>%
  summarize(mean_diff = mean(diff_temp),
            mean_temp = mean(durafet_temp))

log_comp_deploy <- merge_comp
```

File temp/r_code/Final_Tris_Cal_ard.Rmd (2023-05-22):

---
title: "Calculate calibration constants for RED and GREEN DuraFETs on ARDUINO"
author: "Amelia Ritger"
date: "2023-04-07"
output: html_document
---

```{r setup, include=FALSE}
knitr::opts_chunk$set(echo = TRUE)
```

##Load libraries, set constants
```{r}
library(tidyverse)
library(readr)
library(janitor)
library(here)
library(lubridate)

filename_green <- "green_ard_25" #filename for arduino green durafet tris data
filename_red <- "red_ard_25" #filename for arduino red durafet tris data

temp_corr_green <- 0 #1.995
temp_corr_red <- 0 #1.949

#var_ard <- 0 #calculated uncertainties using raw data
#var_ard_real <- 0 #calculated uncertainties using raw data
#var_madg <- 0 #calculated uncertainties using raw data

var_ard <- 0.82869 #calculated uncertainties using raw data
var_ard_real <- 0.16565 #calculated uncertainties using raw data
var_madg <- 0.16978 #calculated uncertainties using raw data

##Correction values for NOT swapped sensors
#ard_correction_m <- 1+0.099 #slope coefficient for arduino (corrected with HOBO)
#ard_correction_b <- -0.632
#madg_correction_m <- 1+0.106 #slope coefficient for madgetech (corrected with #HOBO)
#madg_correction_b <- 0.123

#Correction values for SWAPPED sensors - don't trust these fully because N=1, "too perfect" correction of data
#madg_correction_m <- 1-0.43 #.425 #slope coefficient for madgetech (corrected with HOBO)
#madg_correction_b <- -8.7
#ard_correction_m <- 1-0.51 #.511 #slope coefficient for arduino (corrected with HOBO)
#ard_correction_b <- -10.5

 madg_correction_m <- 1 #slope coefficient for madgetech (corrected with HOBO)
 madg_correction_b <- 0
 ard_correction_m <- 1 #slope coefficient for arduino (corrected with HOBO)
 ard_correction_b <- 0
```

## Run "Ideal" calibration for Green DuraFET tris
```{r}
#Run the code
trisdata_all <- read_csv(here("data", "raw", "april-green", paste(filename_green,".csv",sep=""))) %>%
  #mutate("J4" = rawdata_all[12]-rawdata_all[18]) %>%
  clean_names() %>% # read in tris data excel file
  mutate(date_lubridate=mdy(date)) %>% # tell R "date" is a DATE
  mutate(time_lubridate=hms(time)) %>% # tell R "time" is a TIME
  unite(date_time, c(date, time), sep = " ", remove = TRUE) %>% # combine the date and time columns
  mutate(date_time_lubridate=mdy_hms(date_time)) %>%# tell R "date_time" is a DATE and a TIME
  mutate(j4 = j4_oversampled_mean_m_v - j4_oversampled_mean_m_v_2)

trisdata <- trisdata_all %>%
  select(24, 3,8,9,25) %>%
  setNames(c("date_time", "v1", "v2", "v3", "v4"))

tris_voltages <- data.frame(trisdata$v1,trisdata$v2,trisdata$v3,trisdata$v4) %>% # create OMEGAS data frame with the raw voltages
  mutate(mv1=as.numeric(trisdata.v1),
         mv2=as.numeric(trisdata.v2),
         mv3=as.numeric(trisdata.v3),
         mv4=as.numeric(trisdata.v4)) %>% # changing data to numeric arguments
  select(mv1, mv2, mv3, mv4) # cleaning data frame

omegas_temp_tris <- tris_voltages %>% # create new data frame using omegas values
  mutate(v1=(mv1/1000),
         v2=(mv2/1000),
         v3=(mv3/1000),
         v4=(mv4/1000)) %>% # converting the mV to volts
  mutate(vbattery=((v2/100)*101.57)) %>% # calculate vbattery
  mutate(z=(v4/100)+vbattery*((15000*1)/((1000000*1)+(15000*1)))) %>% # calculate column k
  mutate(y=(z*(1000000*1))) %>% # calculate column l
  mutate(rthermistor=(y/(vbattery-z))) %>% # calculate Rthermistor
  mutate(sh_a=as.numeric(0.00106329736674527)) %>% # create column with Steinhart constant A
  mutate(sh_b=as.numeric(0.000251377462346306)) %>% # create column with Steinhart constant B
  mutate(sh_c=as.numeric(2.55455247726963E-08)) %>% # create column with Steinhart constant C
  mutate(k=(1/(sh_a+sh_b*log(rthermistor)+sh_c*(log(rthermistor))^3))) %>% # create column to calculate intermediate value K
  mutate(durafet=as.numeric((k-273.15))) %>% # create new column to calculate durafet therm 
  mutate(durafet=durafet+temp_corr_green) %>% # do temperature correction
  mutate(durafet=((durafet*ard_correction_m)-ard_correction_b)) %>% #do temperature correction
  mutate(calt=as.numeric(1.0086*durafet+0.3157)) # create Cal_T column (does not get used for further calibration)

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

tris_ph_template <- data.frame(temp,b,c,d,e,f,g,h,i,j,t,k,m)%>% # create tris pH template as a data frame with all above columns
  mutate(n=(b-(c*m)-(d*m*m))*1/t) %>% # create column n
  mutate(o=(-e+(f*m)+(g*m*m))) %>% # create column o
  mutate(p=(h-(i*m))*log(t)-(j*(t))) %>% # create column p
  mutate(trisph=(n+o+p)) # calculate tris pH, add as a new column to tris pH template data frame

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

calibration_values <- omegas_ph_tris %>% # work in omegas_calibration dataframe
  filter(row_number()!=c(1:100)) %>% # remove the first 100 rows (first 20 minutes of data)
  slice_min(tempdiff,n=10) %>% # select the rows that contains the minimum values of change in temperature over time 
  slice_min(phdiff,n=1) %>% # select the row that contains the minimum value of change in pH over time in within the 10 lowest temp differences
  mutate(diff_omegasph = (omegasph - mean(omegasph))) %>%
  slice_min(diff_omegasph)

#Append identifying information before writing .csv
omegas_ph_tris <- omegas_ph_tris %>%
  mutate(logger = "arduino",
         tolerance = "ideal") %>%
  rename("date_time" = "trisdata.date_time",
         "durafet_temp" = "omegas_temp_tris.durafet",
         "v1" = "omegas_temp_tris.v1")

calibration_values <- calibration_values %>%
  mutate(logger = "arduino",
         tolerance = "ideal") %>%
  rename("date_time" = "trisdata.date_time",
         "durafet_temp" = "omegas_temp_tris.durafet",
         "v1" = "omegas_temp_tris.v1")

#Write out .csv files
write.csv(omegas_ph_tris, here("data", "calibrated","calibration-file", paste(filename_green,"_omegas.csv", sep="")),row.names = FALSE) # create csv with calibrated values
write.csv(calibration_values, here("data", "calibrated", paste(filename_green,"_omegas_calib.csv", sep="")),row.names=FALSE)
```

## Run "Ideal" calibration for red DuraFET tris
```{r}
#Run the code
trisdata_all <- read_csv(here("data", "raw", "april-red", paste(filename_red,".csv",sep=""))) %>%
  #mutate("J4" = rawdata_all[12]-rawdata_all[18]) %>%
  clean_names() %>% # read in tris data excel file
  mutate(date_lubridate=mdy(date)) %>% # tell R "date" is a DATE
  mutate(time_lubridate=hms(time)) %>% # tell R "time" is a TIME
  unite(date_time, c(date, time), sep = " ", remove = TRUE) %>% # combine the date and time columns
  mutate(date_time_lubridate=mdy_hms(date_time)) %>%# tell R "date_time" is a DATE and a TIME
  mutate(j4 = j4_oversampled_mean_m_v - j4_oversampled_mean_m_v_2)

trisdata <- trisdata_all %>%
  select(24, 3,8,9,25) %>%
  setNames(c("date_time", "v1", "v2", "v3", "v4"))

tris_voltages <- data.frame(trisdata$v1,trisdata$v2,trisdata$v3,trisdata$v4) %>% # create OMEGAS data frame with the raw voltages
  mutate(mv1=as.numeric(trisdata.v1),
         mv2=as.numeric(trisdata.v2),
         mv3=as.numeric(trisdata.v3),
         mv4=as.numeric(trisdata.v4)) %>% # changing data to numeric arguments
  select(mv1, mv2, mv3, mv4) # cleaning data frame

omegas_temp_tris <- tris_voltages %>% # create new data frame using omegas values
  mutate(v1=(mv1/1000),
         v2=(mv2/1000),
         v3=(mv3/1000),
         v4=(mv4/1000)) %>% # converting the mV to volts
  mutate(vbattery=((v2/100)*101.57)) %>% # calculate vbattery
  mutate(z=(v4/100)+vbattery*((15000*1)/((1000000*1)+(15000*1)))) %>% # calculate column k
  mutate(y=(z*(1000000*1))) %>% # calculate column l
  mutate(rthermistor=(y/(vbattery-z))) %>% # calculate Rthermistor
  mutate(sh_a=as.numeric(0.00106329736674527)) %>% # create column with Steinhart constant A
  mutate(sh_b=as.numeric(0.000251377462346306)) %>% # create column with Steinhart constant B
  mutate(sh_c=as.numeric(2.55455247726963E-08)) %>% # create column with Steinhart constant C
  mutate(k=(1/(sh_a+sh_b*log(rthermistor)+sh_c*(log(rthermistor))^3))) %>% # create column to calculate intermediate value K
  mutate(durafet=as.numeric((k-273.15))) %>% # create new column to calculate durafet therm 
  mutate(durafet=durafet+temp_corr_red) %>% # do temperature correction
  mutate(durafet=((durafet*madg_correction_m)-madg_correction_b)) %>% #do temperature correction
  mutate(calt=as.numeric(1.0086*durafet+0.3157)) # create Cal_T column (does not get used for further calibration)

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

tris_ph_template <- data.frame(temp,b,c,d,e,f,g,h,i,j,t,k,m)%>% # create tris pH template as a data frame with all above columns
  mutate(n=(b-(c*m)-(d*m*m))*1/t) %>% # create column n
  mutate(o=(-e+(f*m)+(g*m*m))) %>% # create column o
  mutate(p=(h-(i*m))*log(t)-(j*(t))) %>% # create column p
  mutate(trisph=(n+o+p)) # calculate tris pH, add as a new column to tris pH template data frame

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

calibration_values <- omegas_ph_tris %>% # work in omegas_calibration dataframe
  filter(row_number()!=c(1:100)) %>% # remove the first 100 rows (first 20 minutes of data)
  slice_min(tempdiff,n=10) %>% # select the rows that contains the 10 minimum values of change in temperature over time 
  slice_min(phdiff,n=1) # select the row that contains the minimum value of change in pH over time in within the 10 lowest temp differences

#Append identifying information before writing .csv
omegas_ph_tris <- omegas_ph_tris %>%
  mutate(logger = "arduino",
         tolerance = "ideal") %>%
  rename("durafet_temp" = "omegas_temp_tris.durafet",
         "v1" = "omegas_temp_tris.v1")

calibration_values <- calibration_values %>%
  mutate(logger = "arduino",
         tolerance = "ideal") %>%
  rename("durafet_temp" = "omegas_temp_tris.durafet",
         "v1" = "omegas_temp_tris.v1")

#Write out .csv files
write.csv(omegas_ph_tris, here("data", "calibrated", "calibration-file", paste(filename_red,"_omegas.csv", sep="")),row.names = FALSE) # create csv with calibrated values
write.csv(calibration_values, here("data", "calibrated", paste(filename_red,"_omegas_calib.csv", sep="")),row.names=FALSE)
```

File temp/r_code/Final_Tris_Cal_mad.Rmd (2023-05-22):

---
title: "Calculate calibration constants for RED and GREEN DuraFETs on MADGETECH"
author: "Amelia Ritger"
date: "2023-04-07"
output: html_document
---

```{r setup, include=FALSE}
knitr::opts_chunk$set(echo = TRUE)
```

##Load libraries, set constants
```{r}
library(tidyverse)
library(readr)
library(janitor)
library(here)
library(lubridate)

filename_green <- "green_mad_25" #filename for madgetech green durafet tris data
filename_red <- "red_mad_25" #filename for madgetech red durafet tris data

temp_corr_green <- 0 #1.995
temp_corr_red <- 0 #1.949

#var_ard <- 0 #calculated uncertainties using raw data
#var_ard_real <- 0 #calculated uncertainties using raw data
#var_madg <- 0 #calculated uncertainties using raw data

var_ard <- 0.82869 #calculated uncertainties using raw data
var_ard_real <- 0.16565 #calculated uncertainties using raw data
var_madg <- 0.16978 #calculated uncertainties using raw data

##Correction values for NOT swapped sensors
#ard_correction_m <- 1+0.099 #slope coefficient for arduino (corrected with HOBO)
#ard_correction_b <- -0.632
#madg_correction_m <- 1+0.106 #slope coefficient for madgetech (corrected with #HOBO)
#madg_correction_b <- 0.123

#Correction values for SWAPPED sensors - don't trust these fully because N=1, "too perfect" correction of data
#madg_correction_m <- 1-0.43 #.425 #slope coefficient for madgetech (corrected with HOBO)
#madg_correction_b <- -8.7
#ard_correction_m <- 1-0.51 #.511 #slope coefficient for arduino (corrected with HOBO)
#ard_correction_b <- -10.5

 madg_correction_m <- 1 #slope coefficient for madgetech (corrected with HOBO)
 madg_correction_b <- 0
 ard_correction_m <- 1 #slope coefficient for arduino (corrected with HOBO)
 ard_correction_b <- 0
```

## Run "Ideal" calibration for Green DuraFET tris
```{r}
#Run the code
trisdata <- read_csv(here("data", "raw", "april-green", paste(filename_green,".csv",sep=""))) %>%
    filter(row_number()!=c(1:5)) %>% # remove the first 5 rows
  row_to_names(row_number=1) %>% # make the top row the column headers
  rename("Date"=1,
         "Time"=2) %>% # rename date and time columns
  clean_names() %>% # read in tris data excel file
  mutate(date_lubridate=mdy(date)) %>% # tell R "date" is a DATE
  mutate(time_lubridate=hms(time)) %>% # tell R "time" is a TIME
  unite(date_time, c(date, time), sep = " ", remove = TRUE) %>% # combine the date and time columns
  mutate(date_time_lubridate=mdy_hms(date_time)) # tell R "date_time" is a DATE and a TIME

tris_voltages <- data.frame(trisdata$voltage_1_m_v,trisdata$voltage_2_m_v,trisdata$voltage_3_m_v,trisdata$voltage_4_m_v) %>% # create OMEGAS data frame with the tris voltages
  mutate(mv1=as.numeric(trisdata.voltage_1_m_v),
         mv2=as.numeric(trisdata.voltage_2_m_v),
         mv3=as.numeric(trisdata.voltage_3_m_v),
         mv4=as.numeric(trisdata.voltage_4_m_v)) %>% # changing data to numeric arguments
  select(mv1, mv2, mv3, mv4) # cleaning data frame

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

tris_ph_template <- data.frame(temp,b,c,d,e,f,g,h,i,j,t,k,m)%>% # create tris pH template as a data frame with all above columns
  mutate(n=(b-(c*m)-(d*m*m))*1/t) %>% # create column n
  mutate(o=(-e+(f*m)+(g*m*m))) %>% # create column o
  mutate(p=(h-(i*m))*log(t)-(j*(t))) %>% # create column p
  mutate(trisph=(n+o+p)) # calculate tris pH, add as a new column to tris pH template data frame

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

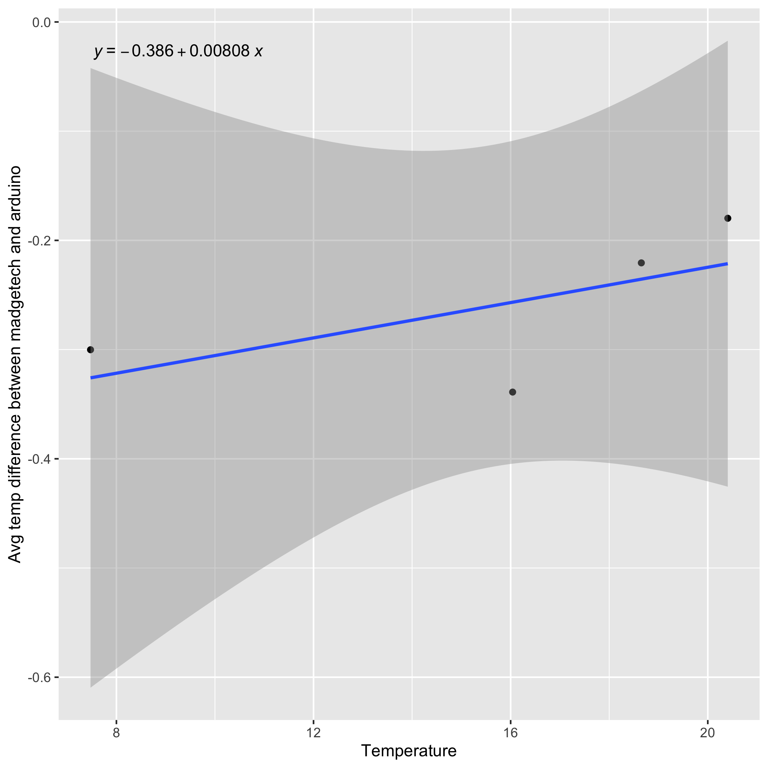
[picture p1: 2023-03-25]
temp/figures/correction/arduino-temp_all.png

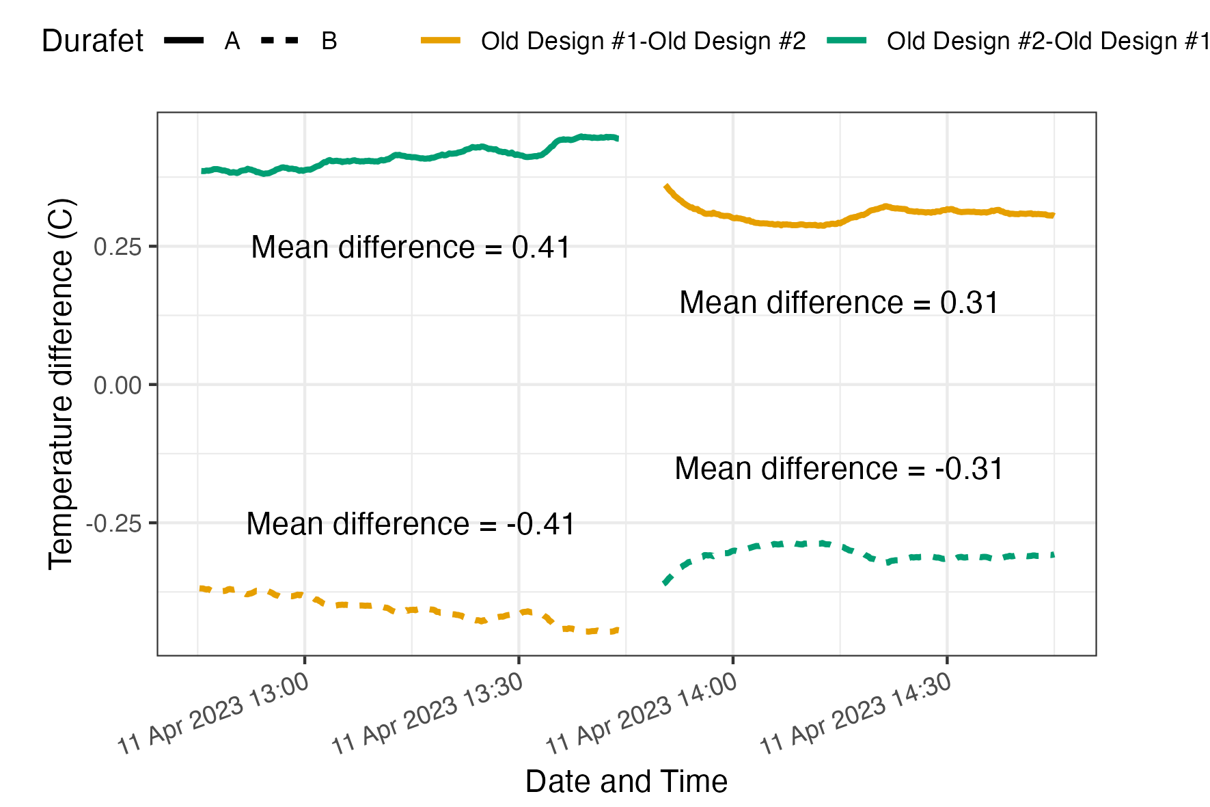
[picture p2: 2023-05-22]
temp/figures/final/tempMAD-MAD.png

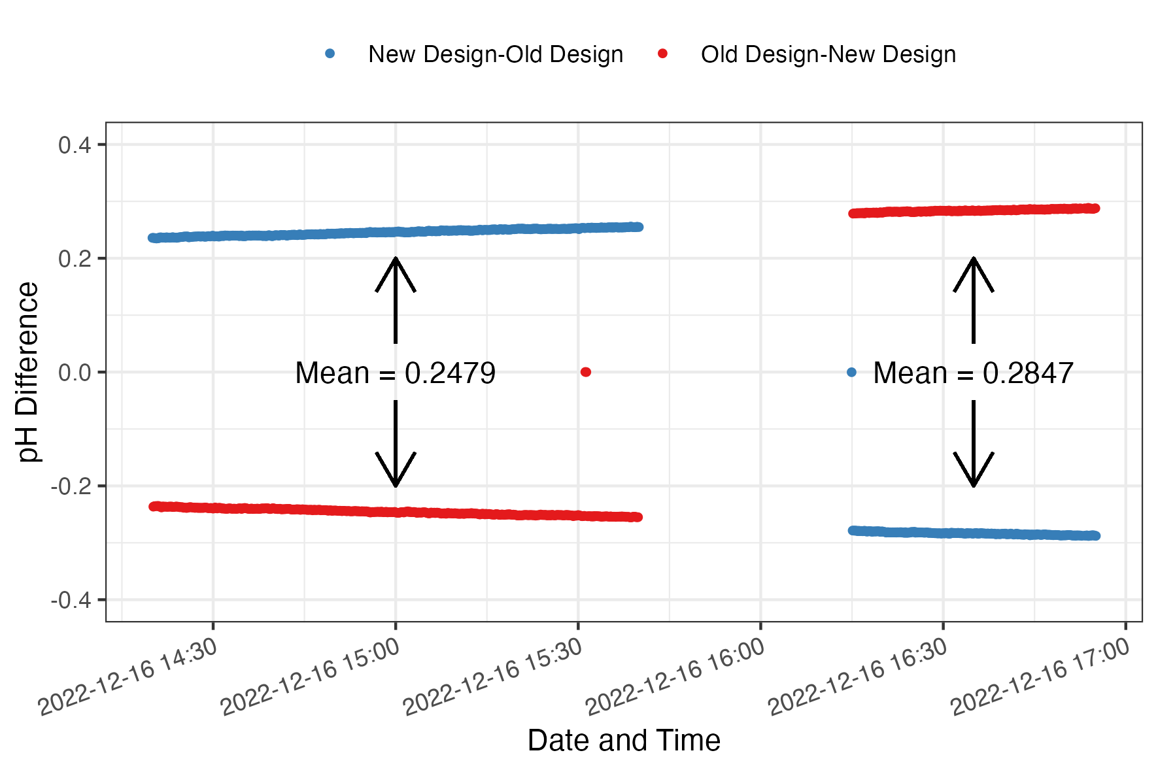
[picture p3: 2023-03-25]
temp/figures/final/swap-ph_diff.png

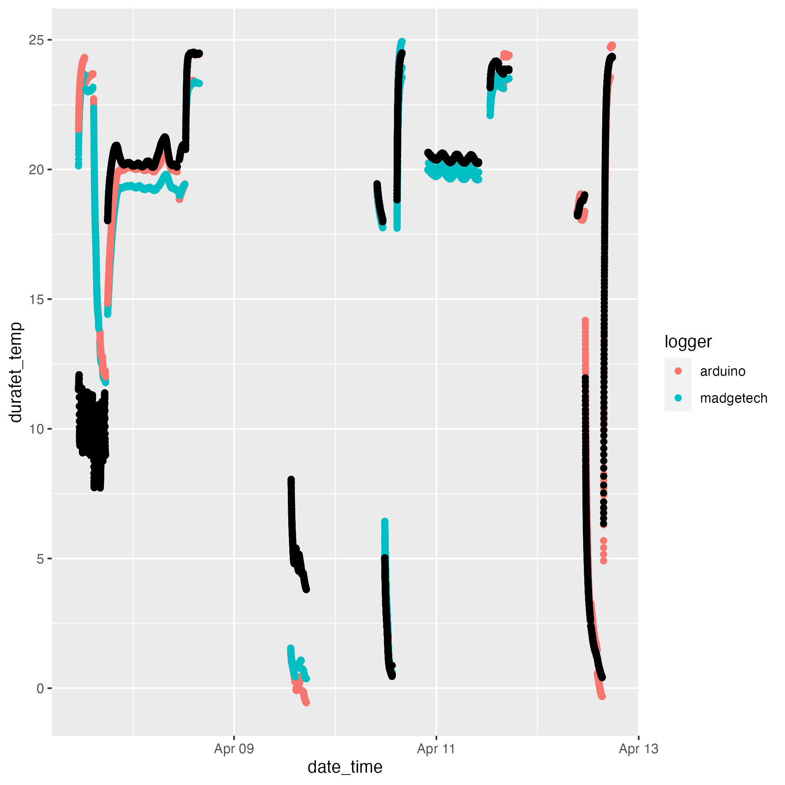
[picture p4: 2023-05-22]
temp/figures/final/all_correction.png

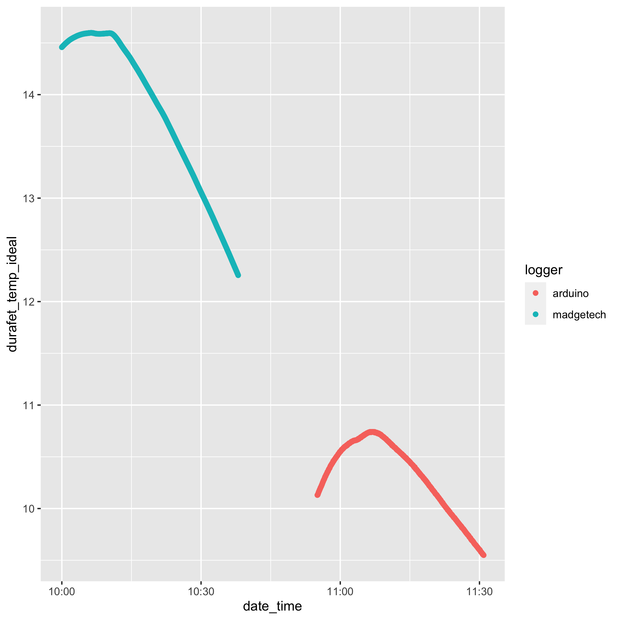
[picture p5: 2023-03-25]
temp/figures/swap/fridge-temp.png

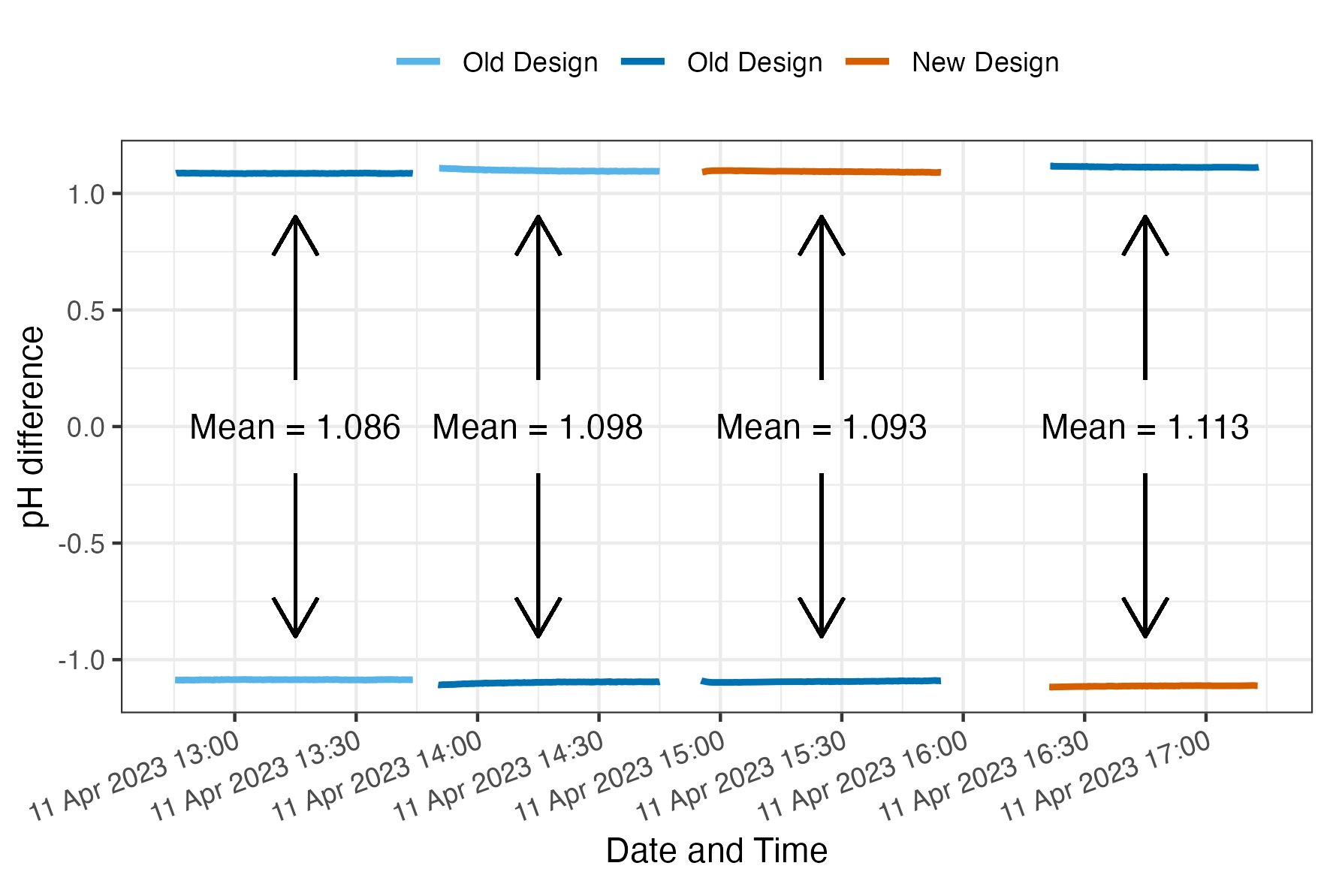
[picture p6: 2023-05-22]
temp/figures/final/FINAL-ph-difference.png

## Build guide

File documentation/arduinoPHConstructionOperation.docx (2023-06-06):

Arduino pH sensor project

Amelia Ritger

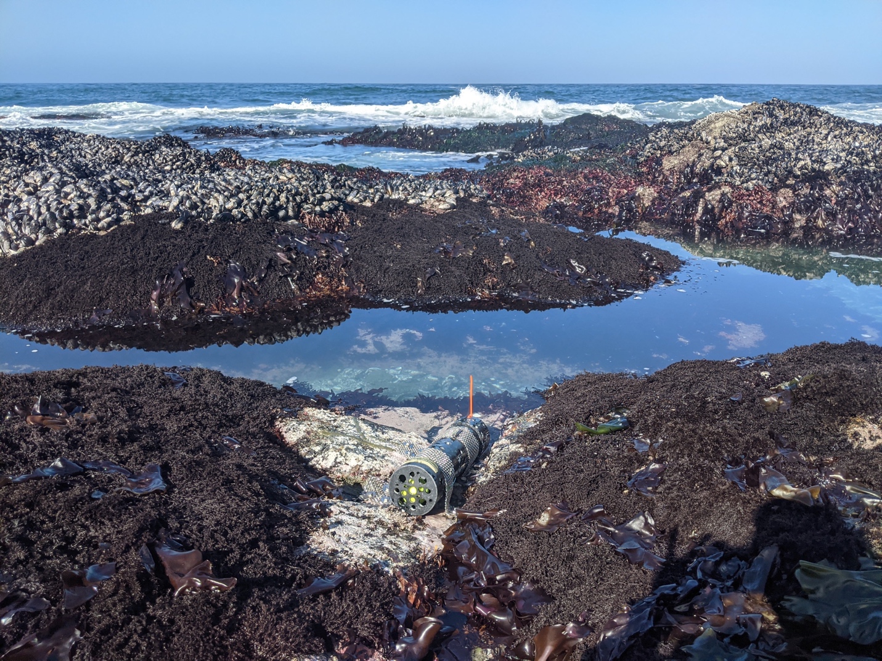
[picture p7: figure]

This work is licensed under the Apache License 2.0 (https://github.com/ameliaritger/arduino-ph-sensor/blob/main/LICENSE).

Contents

1. Introduction
2. Materials, Tools, and Consumables
3. Voltage divider circuit schematic
4. Component layout on FeatherWing
5. Preparing the Arduino
6. Preparing the battery pack
7. Communicating with the Arduino
8. Deploying the Arduino

1. Introduction

Ocean acidification monitoring efforts are a crucial component of tracking the impacts of climate change in marine ecosystems. However, the high instrument cost presents a major barrier to the production of scientific knowledge and has resulted in a highly fragmented understanding of the global progression of acidification. Our project built upon an existing nearshore marine pH sensor design which utilizes a Durafet pH electrode. Our goal was to lower barriers to access by significantly lowering the cost of, and improving approachability to, the design and use of pH sensor electronics. We have created a more compact design using open-source components based on the popular and easy-to-use Arduino platform that eliminates over $900 from the cost of the sensor electronics. We demonstrate with lab and field testing that switching to Arduino-based sensor electronics maintains high data fidelity. Our design supports open science by allowing more individuals and research groups to engage in high-quality oceanographic research.

This document provides guidance on the construction of the data-logger electronics associated with the Durafet-based pH sensor. This document is a work in progress, please stay tuned for updates!

2. Materials, Tools, and Consumables

ITEM | QUANTITY | PRICE

Tools
Wire strippers | 1 | TBA
Soldering iron | 1 | TBA
Multimeter | 1 | TBA
Needle nose pliers | 1 | TBA
Flush cutters | 1 | TBA
Solderless breadboard | 1 | TBA

Materials
Adafruit Feather M0 Adalogger | 1 | $19.95 (https://www.adafruit.com/product/2796)
Adafruit FeatherWing Proto | 1 | $4.95 (https://www.adafruit.com/product/2884)
Adafruit ADS1015 12-bit ADC | 1 | $9.95 (https://www.adafruit.com/product/1083)
Adafruit ADS1115 16-bit ADC | 1 | $14.95 (https://www.adafruit.com/product/1085)
Adafruit DS3231 Precision RTC | 1 | $17.50 (https://www.adafruit.com/product/3013)
2-AA battery holder | 1 | $0.53 (https://www.digikey.com/en/products/detail/nte-electronics-inc/23-BH2-3/16499222)
AA batteries | 2 | TBA
micro-USB cable | 1 | TBA
microSD card (256 - 512 MB or higher) | 1 | TBA
microSD card reader | 1 | $5.95 (https://www.adafruit.com/product/939)
1 M Ω resistor | 5 | TBA
15 kΩ resistor | 1 | TBA
10 kΩ resistor | 2 | TBA
20 μF capacitor | 1 | TBA
100 μF capacitor | 3 | TBA

Consumables
Lead-free solder | 1 | TBA
Electrical tape | 1 | TBA
22 AWG solid core wire | 1 | $2.95 (https://www.adafruit.com/product/290)
22 AWG stranded core wire | 1 | $2.95 (https://www.adafruit.com/product/2997)
Crimps | 10 | $2.29 (https://www.digikey.com/en/products/detail/te-connectivity-amp-connectors/104479-8/)
90 degree male pin header (3 position) | 1 | $1.08 (https://www.digikey.com/en/products/detail/te-connectivity-amp-connectors/103634-2/291595)
Female pin socket (3 position) | 1 | $0.55 (https://www.digikey.com/en/products/detail/te-connectivity-amp-connectors/104257-2/)
Vertical male pin header (6 position) | 1 | $0.85 (https://www.digikey.com/en/products/detail/te-connectivity-amp-connectors/103638-5/)
Female pin socket (6 position) | 1 | $0.59 (https://www.digikey.com/en/products/detail/te-connectivity-amp-connectors/104257-5/)
Stacking female headers | 1 | $1.25 (https://www.adafruit.com/product/2830)
Nylon screws | 1 | $16.95 (https://www.adafruit.com/product/3299)
Dupont cables (M-M) | 1 | $1.95 (https://www.adafruit.com/product/1956)
Dupont cables (M-F) | 1 | $1.95 (https://www.adafruit.com/product/1953)

3. Voltage divider circuit schematic

The voltage divider, originally designed by Gernot Friederich at Monterey Bay Aquarium Research Institute, joins the Durafet pH electrode to the ADC inputs. The resistor values used are 1 M Ω (R1, R4, R5, R6, R7), 10 kΩ (R2, R3), and 15 kΩ (R8). The capacitor values used are 20 μF (C1) and 100 μF (C2, C3, C4), although substituting C1 with a 22 μF capacitor is acceptable.

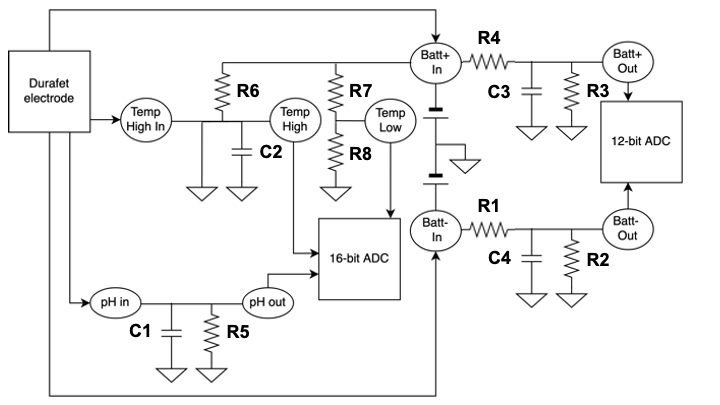
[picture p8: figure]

Fig GG. Circuit schematic of the voltage divider circuits joining the Durafet electrode to the ADC inputs.

4. Component layout on FeatherWing

Cost savings are maximized with the DIY build by soldering all components of the voltage divider. This is the most challenging soldering step of the build, as it requires a steady hand and thoughtful consideration of the order in which components are soldered. You must plan ahead with layering components as you solder, as some components overlap with wiring/solder bridge connections. We highly recommend laying out the components on a breadboard and testing connections with a multimeter and with the Arduino IDE prior to soldering to ensure the system is operating correctly.

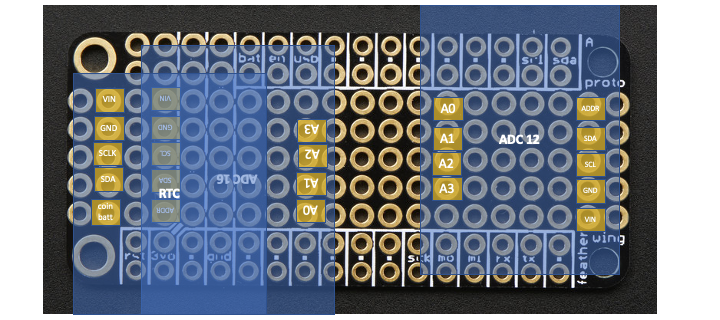
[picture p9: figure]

Fig AA. Diagram of ADC (ADS1115 and ADS1015) and RTC (DS3231) alignment on front side of FeatherWing.

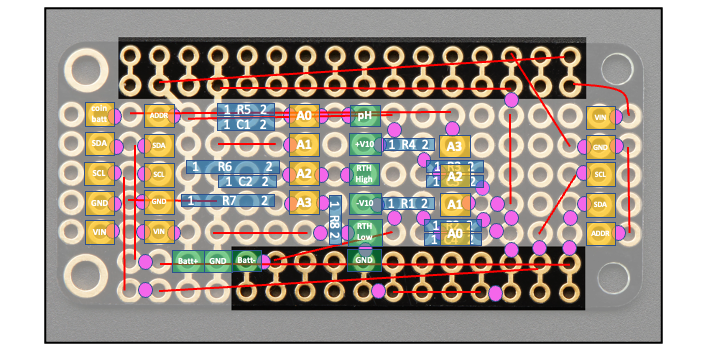
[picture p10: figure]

Fig BB. Diagram of all RTC and ADC pins (yellow), passive components (blue), PCB mount headers (green), and wiring (red)/solder bridge (pink) connections on back side of FeatherWing.

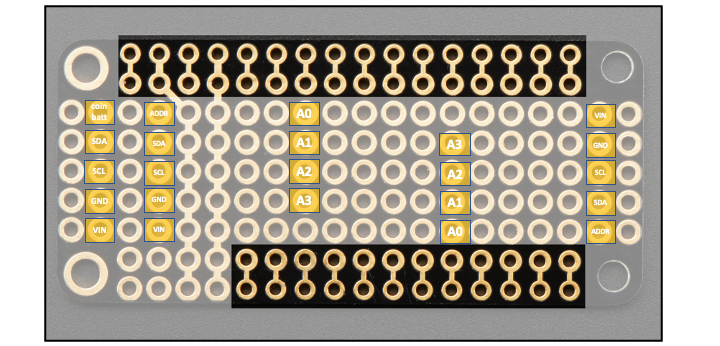
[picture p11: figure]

Fig CC. Alignment of only RTC and ADC pins on back side of FeatherWing.

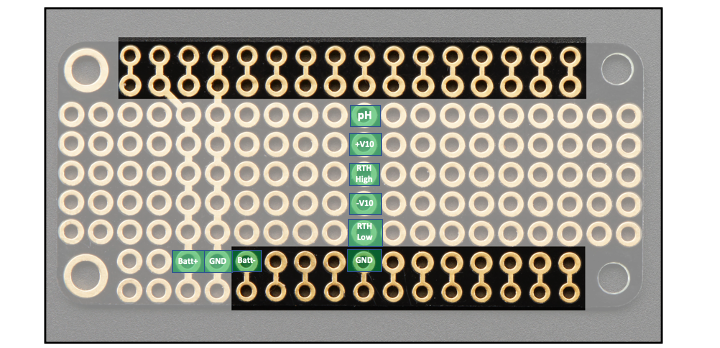
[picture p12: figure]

Fig DD. Alignment of only PCB mount headers on back side of FeatherWing.

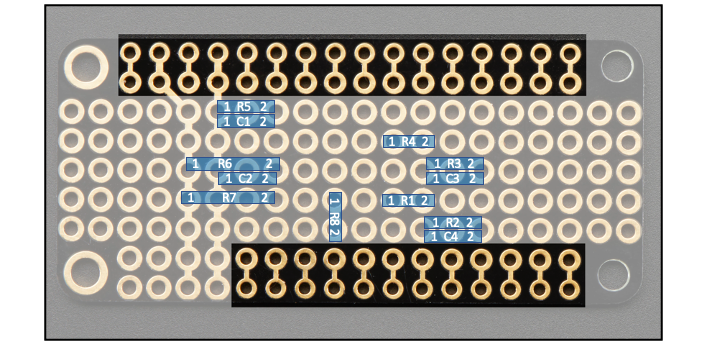
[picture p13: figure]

Fig EE. Alignment of only resistors and capacitors on back side of FeatherWing. See Section XX for details on component values.

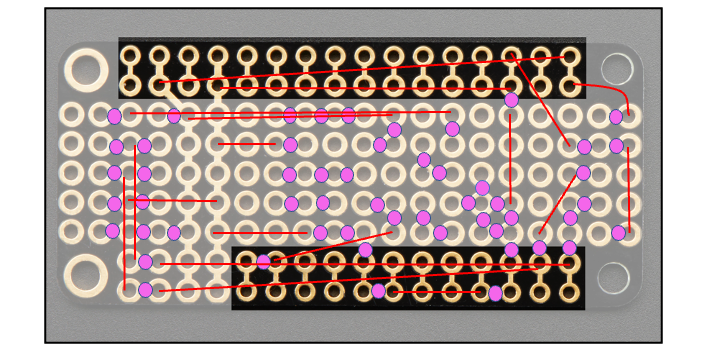
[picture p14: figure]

Fig FF. Alignment of wiring and solder bridges between pads on back side of FeatherWing.

5. Preparing the Arduino

This project uses an Adalogger M0 paired with a real-time clock (RTC) and two analog-to-digital converters (ADCs). Together, these components allow users to log timestamped Durafet data onto a microSD card. The ADCs have differential channels which allow the Adalogger to read negative voltages from the Durafet's pH and battery inputs.

The following paragraph has been copied over from the Oceanography for Everyone OpenCTD project documentation, as they also use the Adalogger M0 and have done an excellent job of explaining the process of preparing the Adalogger for assembly. You can find the full documentation associated with OpenCTD, which includes step by step instructions and pictures of the soldering process, at the following link: https://oceanographyforeveryone.com/project/openctd/.

The Adalogger and RTC (and ADCs) will need headers. Headers are the male or female pin assemblies that allow you to connect and disconnect electronic. A “pin” refers to any electrical contact point and will generally be used in this guide to refer to the holes in circuit boards through which wires, headers, and other components will be soldered. You will be soldering components directly to a circuit board. Assembling the Adalogger and Real-Time Clock (and ADCs) is a good, low-risk, opportunity to practice your soldering skills.

6. Preparing the battery pack

Cut a piece of stranded core wire and solder it to the metal wire between the two battery cells. This wire is now your GND, the red wire is your Batt+ and the black wire is your Batt-.

7. Communicating with the Arduino

The following paragraph has been copied over from the Oceanography for Everyone OpenCTD project documentation, as they also use the Adalogger M0 and have done an excellent job of explaining the process of communicating with the Adalogger. You can find the full documentation associated with OpenCTD, which includes step by step instructions about the process of using the Arduino IDE with the Adalogger, at the following link: https://oceanographyforeveryone.com/project/openctd/.

To prepare your computer to talk to the M0 Adalogger, download and install Arduino IDE (https://www.arduino.cc/en/Main/Software). You will need to install additional boards so that Arduino IDE will be able to recognize the Adalogger. For a detailed walkthrough of this process, with screenshots included, please visit: https://learn.adafruit.com/adafruit-feather-m0- adalogger/setup. Please be aware that the Arduino, Adafruit, or Github Software may have been updated more recently than this manual and that the location of certain tools and functions may differ from the instructions.

You will also need to manually download and install the following libraries for this project:

- Adafruit_ADS1X15.h
- ArduinoLowPower.h
- DS3232RTC.h
- Streaming.h
- Time.h
- SdFat.h

Please refer to https://www.arduino.cc/en/Guide/Libraries for detailed instructions for installing libraries.

You will want to use the serial monitor in Arduino IDE to verify that everything is working correctly. You should see messages about a successful SD card initialization and a successful creation of a new file and header on the SD card. You can then unplug the Arduino from your computer, remove the SD card, and confirm that data was recorded on the SD card.

Deploying the Arduino ("arduinoCode")

The project GitHub repository includes CONFIG.h and SRC.h files alongside a main arduinoCode.ino file, all of which are essential for proper communication and deployment. You should only be editing the CONFIG file for deployment.

To change the file name printed to the SD card, edit the contents within the parentheses on line 4. The filename must be equal or less than 8 characters and must have a .csv file extension. Default: "filename.csv".

To change the sampling interval, edit the number within the curly brackets on line 6. This number represents the frequency of sampling in seconds. For example, if you want sampling to occur once every 30 minutes, you will set this number to 1800. Default: 600.

To change the deployment start time and date, edit the numbers within the curly brackets on lines 7-9. These numbers represent start date (line 7), and start time in hours (line 8) and minutes (line 9). For example, if you want sampling to occur on the third day of the month at noon, you will set these numbers to 3, 12, 0. Use the numbering intervals recommended in the comments (e.g., 0, not 00, to start sampling at the top of the hour). Default: 12, 0, 0.

To match the RTC time with your computer time, edit the number on line 15. This "fudge factor" represents a number, in seconds, and allows for fine-scale tuning of the timestamp printed to the SD card. Open up the Serial while the Arduino is running to check the difference between timestamp printed on the Serial monitor (left) and the timestamp of the RTC that is printed on the SD card (right of the colon). Alter the fudge factor so that the value of the RTC timestamp aligns with your computer/Serial time, and run the code again to check for alignment. For example, if the Serial timestamp is 5 seconds ahead of the RTC timestamp, then add 5 to the "fudge factor". The fudge factor addresses differences in Arduino code upload times when using different computers - typically, faster processors will have smaller fudge factors (0-10) while slower processors can have fudge factor values higher than 15. Note: Uploading code to the Arduino on a new day will often take significantly longer than subsequent uploads, and so it is recommended that you upload at least twice to check your fudge factor is correct. Default: 15.

Your Adalogger is now ready for deployment!

Processing the data ("rCode")

After deploying your Adalogger, you will be able to collect the .csv data file from the microSD card. These data can then be imported into an R project alongside the R code found on the project GitHub repository for processing. There are four .Rmd files:

- Final_deploy_voltages.Rmd
- Final_OMEGAS.Rmd
- Final_standardize_data.Rmd
- Final_Tris_Cal.Rmd

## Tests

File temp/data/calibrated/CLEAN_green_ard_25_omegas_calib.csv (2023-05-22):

date_time | durafet_temp | v1 | trisph | tk | st | eot | omegasph | diff | tempdiff | phdiff | diff_omegasph | logger | tolerance
2023-04-07 13:42:00 | 23.4720679161213 | 0.073 | 8.14143368494911 | 296.622067916121 | 0.0588554932241856 | -0.381258626616121 | 7.71820269835836 | 0.42323098659075 | 0 | 0 | -0.000702565194023563 | arduino | ideal

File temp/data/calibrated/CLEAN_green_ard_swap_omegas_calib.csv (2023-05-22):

date_time | durafet_temp | v1 | trisph | tk | st | eot | omegasph | diff | tempdiff | phdiff | diff_omegasph | logger | tolerance
2023-04-11 15:44:45 | 21.5775758494478 | 0.10637 | 8.20132719019375 | 294.727575849448 | 0.0584795897528872 | -0.379364134549448 | 8.3060455212148 | -0.104718331021049 | 0 | 0 | -0.00157542791544074 | arduino | ideal

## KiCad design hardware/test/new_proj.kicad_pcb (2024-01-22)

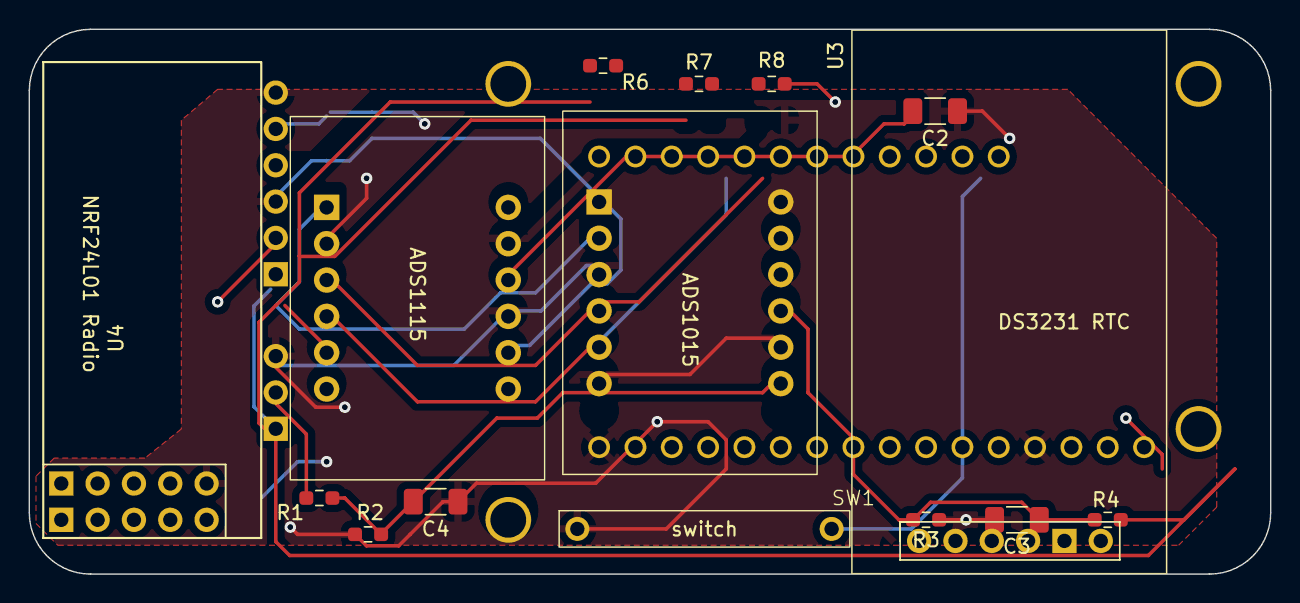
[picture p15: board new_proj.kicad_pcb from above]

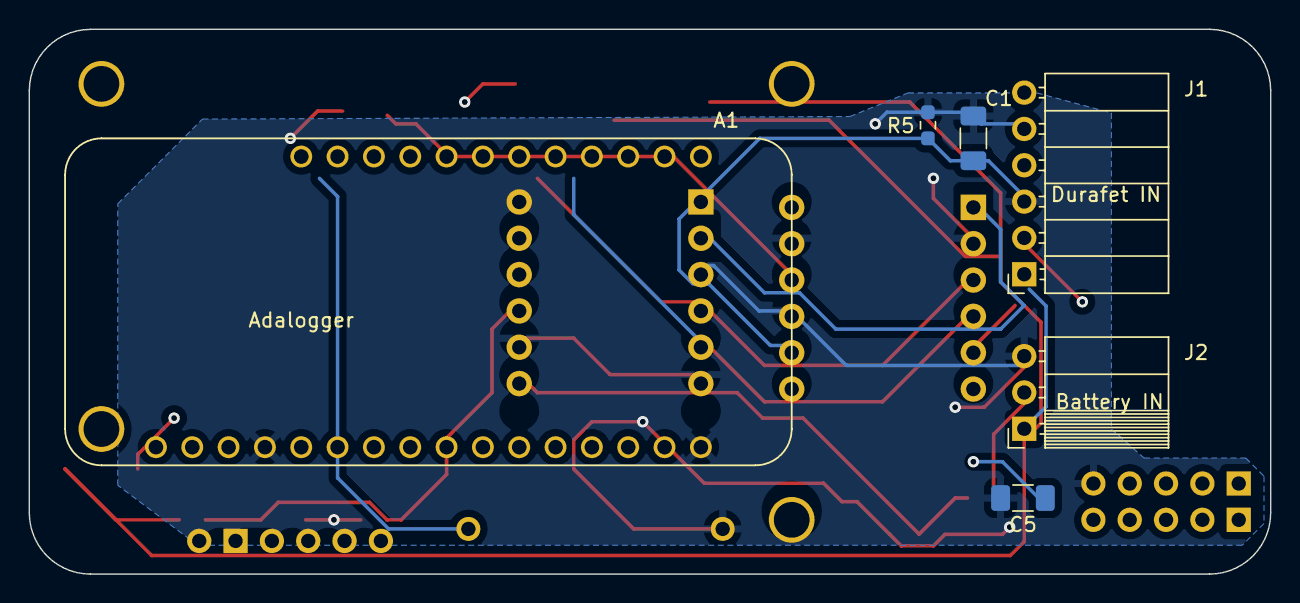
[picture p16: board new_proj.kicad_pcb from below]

Board: 2 copper layers, 86.8 x 38.1 mm, 21 parts (6 on the bottom side), 17 nets.

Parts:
A1: Adafruit_Feather_M0_Adalogger; Adalogger_amelia_nomount
C1: 22uF; C_1206_3216Metric_Pad1.33x1.80mm_HandSolder
C2, C3, C4: 100uF; C_1206_3216Metric_Pad1.33x1.80mm_HandSolder
C5: 10uF; C_1206_3216Metric_Pad1.33x1.80mm_HandSolder
J1: Conn_01x06_Pin; PinSocket_1x06_P2.54mm_Horizontal
J2: Conn_01x03_Pin; PinSocket_1x03_P2.54mm_Horizontal
R1, R4, R5, R6, R7: 1M; R_0603_1608Metric_Pad0.98x0.95mm_HandSolder
R2, R3: 10k; R_0603_1608Metric_Pad0.98x0.95mm_HandSolder
R8: 15k; R_0603_1608Metric_Pad0.98x0.95mm_HandSolder
SW1: SW_Reed; REED_amelia
U1, U2: ADS_Ritger; ADC_amelia_nomount
U3: DS3231MZ; DS3231RTC_amelia
U4: NRF24L01_Breakout; NRF24L01Module

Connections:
+BATT: A1.2 (3V3), C5.1, J1.1, J2.1, R4.1, R6.1, R7.2, U1.1 (VDD), U1.5 (ADDR), U2.1 (VDD), U3.2 (VCC), U4.1 (VCC)
-BATT: J1.2, J2.2, R1.1
GND: A1.4 (GND), A1.16 (GND), C1.2, C2.2, C3.2, C4.2, C5.2, J1.3, J1.6, J2.3, R2.2, R3.2, R5.2, R8.1, SW1.1, U1.2 (GND), U1.8 (AIN3), U1.10 (AIN1), U2.2 (GND), U2.5 (ADDR), U2.10 (AIN1), U3.1 (GND), U4.9 (GND)
MISO: A1.13 (MISO/D22), U4.8 (MISO)
MOSI: A1.12 (MOSI/D23), U4.5 (MOSI)
unnamed: A1.19 (D5), U3.5 (~INT/SQW)
unnamed: A1.20 (D6), U4.4 (CE)
unnamed: A1.22 (D10), U4.3 (~CSN)
unnamed: A1.24 (D12), SW1.2
unnamed: R7.1, R8.2
unnamed: C4.1, R1.2, R2.1, U2.11 (AIN0)
unnamed: C3.1, R3.1, R4.2, U2.9 (AIN2)
RTH_High: C2.1, J1.5, R6.2, U1.9 (AIN2)
SCK: A1.11 (SCK/D24), U4.6 (SCK)
SCL: A1.18 (SCL/D21), U1.3 (SCL), U2.3 (SCL), U3.4 (SCL)
SDA: A1.17 (SDA/D20), U1.4 (SDA), U2.4 (SDA), U3.3 (SDA)
pH: C1.1, J1.4, R5.1, U1.11 (AIN0)

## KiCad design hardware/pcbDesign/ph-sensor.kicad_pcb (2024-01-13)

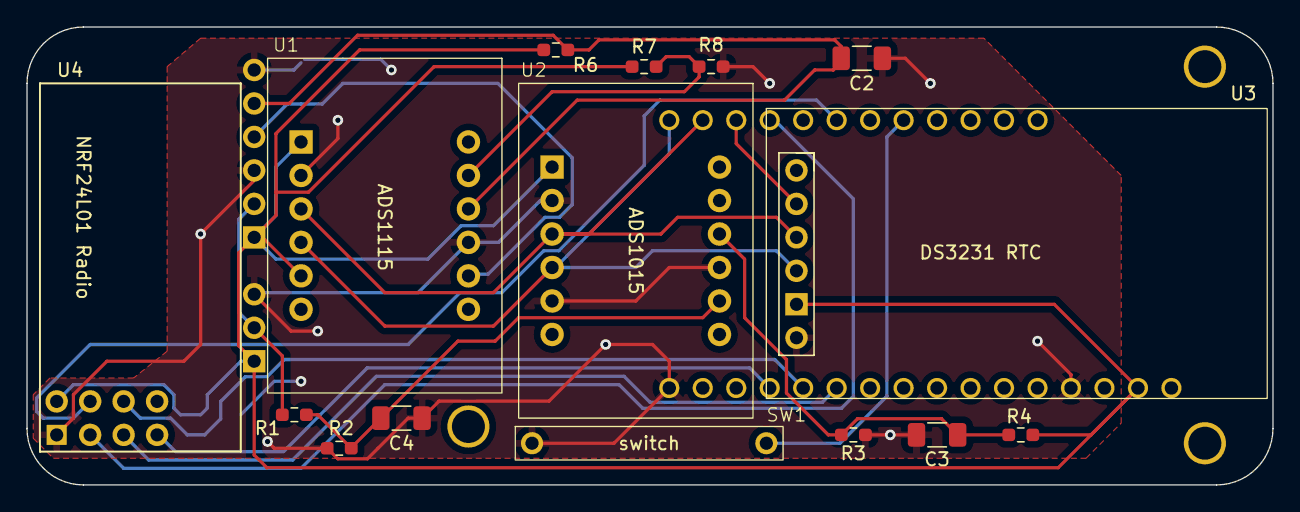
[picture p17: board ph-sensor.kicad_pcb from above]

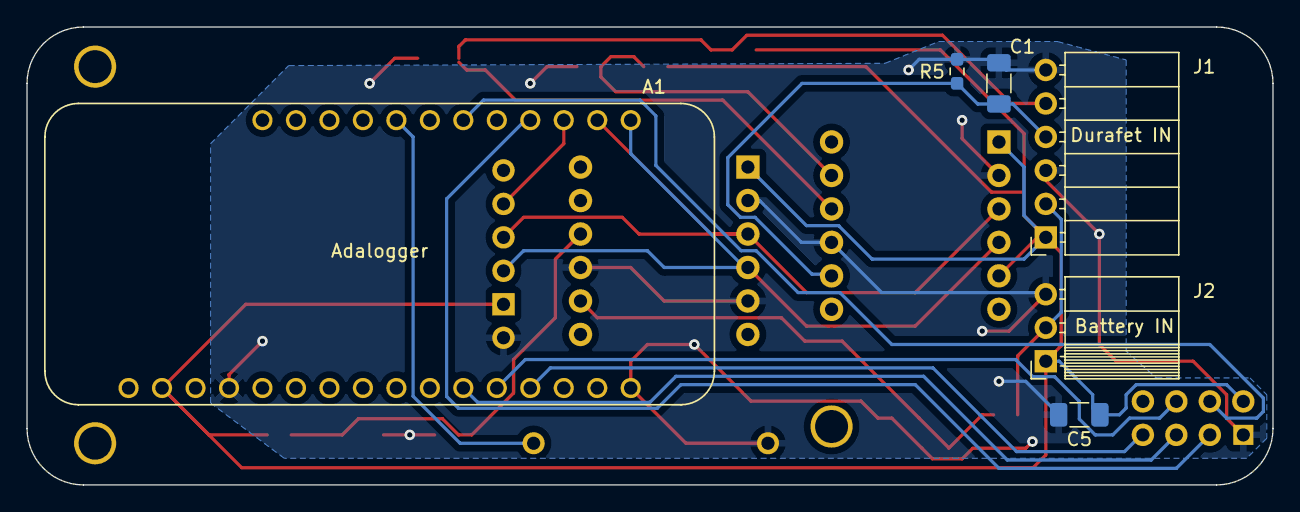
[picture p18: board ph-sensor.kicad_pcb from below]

Board: 2 copper layers, 94.5 x 34.7 mm, 21 parts (6 on the bottom side), 17 nets.

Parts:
A1: Adafruit_Feather_M0_Adalogger; Adalogger_amelia_nomount
C1, C2, C3, C4, C5: C; C_1206_3216Metric_Pad1.33x1.80mm_HandSolder
J1: Conn_01x06_Pin; PinSocket_1x06_P2.54mm_Horizontal
J2: Conn_01x03_Pin; PinSocket_1x03_P2.54mm_Horizontal
R1, R2, R3, R4, R5, R6, R7, R8: R_US; R_0603_1608Metric_Pad0.98x0.95mm_HandSolder
SW1: SW_Reed; REED_amelia
U1, U2: ADS_Ritger; ADC_amelia_nomount
U3: DS3231MZ; DS3231RTC_amelia
U4: NRF24L01_Breakout; NRF24L01Module

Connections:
+BATT: A1.2 (3V3), C5.1, J1.1, J2.1, R4.1, R6.1, R7.2, U1.1 (VDD), U1.5 (ADDR), U2.1 (VDD), U3.5 (VCC), U4.2 (VCC)
-BATT: J1.2, J2.2, R1.1
GND: A1.4 (GND), A1.16 (GND), C1.2, C2.2, C3.2, C4.2, C5.2, J1.3, J1.6, J2.3, R2.2, R3.2, R5.2, R8.1, SW1.1, U1.2 (GND), U1.10 (AIN1), U2.2 (GND), U2.5 (ADDR), U2.10 (AIN1), U3.6 (GND), U4.1 (GND)
MISO: A1.13 (MISO/D22), U4.7 (MISO)
MOSI: A1.12 (MOSI/D23), U4.6 (MOSI)
unnamed: A1.19 (D5), U3.2 (~INT/SQW)
unnamed: A1.20 (D6), U4.3 (CE)
unnamed: A1.22 (D10), U4.4 (~CSN)
unnamed: A1.24 (D12), SW1.2
unnamed: R7.1, R8.2, U1.8 (AIN3)
unnamed: C4.1, R1.2, R2.1, U2.11 (AIN0)
unnamed: C3.1, R3.1, R4.2, U2.9 (AIN2)
RTH_High: C2.1, J1.5, R6.2, U1.9 (AIN2)
SCK: A1.11 (SCK/D24), U4.5 (SCK)
SCL: A1.18 (SCL/D21), U1.3 (SCL), U2.3 (SCL), U3.3 (SCL)
SDA: A1.17 (SDA/D20), U1.4 (SDA), U2.4 (SDA), U3.4 (SDA)
pH: C1.1, J1.4, R5.1, U1.11 (AIN0)

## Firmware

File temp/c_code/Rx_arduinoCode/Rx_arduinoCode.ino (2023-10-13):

// SAMPLE OVER TIME with wireless functionality
// First compiled by Amelia Ritger March 24, 2023
// Last edited
// Maybe make a function for READ ADC section?
// Remove any Serial printing for final publication.
// Remove alarmTrigger and add sleep functionality, maybe move Alarm2 up to setup out of loop since it is a one time thing?
// the slave or the receiver

#include <SPI.h>
#include <Wire.h>

#include <Adafruit_ADS1X15.h>
#include "ArduinoLowPower.h"
#include <DS3232RTC.h>      // https://github.com/JChristensen/DS3232RTC
#include <Streaming.h>      // https://github.com/janelia-arduino/Streaming , allows you to use << formatting
#include <Time.h>           // https://github.com/PaulStoffregen/Time
#include "SdFat.h"          // https://github.com/greiman/SDFat
#include <nRF24L01.h>       // https://nrf24.github.io/RF24/
#include <RF24.h>

#include "CONFIG.h"
#include "SRC.h"

DS3232RTC rtc;            // Construct RTC
#define DS3231_I2C_ADDRESS 0x68 // Needed when we cut VCC line from RTC, see https://github.com/EKMallon/Utilities/blob/master/setTme/setTme.ino
#define DS3231_CONTROL_REG 0x0E

SdFat sd;                 // Construct SD card
File file;                // Construct File for SD card
Adafruit_ADS1015 ads1015; // Construct Ads1015
Adafruit_ADS1115 ads1115; // Construct Ads1115
#define ADS1X15_REG_CONFIG_MODE_SINGLE (0x0100)  // Power down ADCs in single-shot mode

// Define pins
const uint8_t ledPin = 13; // Adalogger internal LED pin
const uint8_t chipSelect = 4; // Adalogger microSD card chip select pin
const uint8_t reedPin = 12; // Reed switch signals on this pin
const uint8_t cePin = 6; // NRF24L01 CE pin
const uint8_t csnPin = 10; // NRF24L01 CSN pin
const uint8_t intPin = 5; // RTC provides an alarm signal on this pin

// Set up Radio
const byte radioAddress[5] = {'R', 'x', 'A', 'A', 'A'};
RF24 radio(cePin, csnPin);
unsigned long dataReceived; // type must match dataToSend in Tx
byte ackData[32] = {0}; // the SD card file values to be sent to Tx; 32 bytes max for NRF24L01
const uint16_t dataDivisible = 1000; // minimum divisible value for dataReceived value

// Initialize RTC variables
char timestamp[32]; // Current time from the RTC in text format, 32 bytes long
bool alarmTrigger = true; // Create variable set to false for alarm nesting. Set to true if you want immediate start time.

// Initialize other variables
int ledState = LOW; // ledState used to set the LED
bool newData = false;
bool newSdData = true;
bool triggerState = false;
bool radioPowerState = false;
int reedState;

// Initialize ADC variables
int16_t adc2_1, adc2_2, adc2_diff, adc1_1, adc1_diff; //adc1_2 for coin batt
int oversampleArray[OVERSAMPLE_VALUE]; // generate array for oversampling
int oversampleMin, oversampleMax;
float oversampleMean;
double oversampleSD;

// Initialize millis variables
unsigned long previousMillisRadio = 0;
unsigned long previousMillisReed = 0;
unsigned long previousMillisBlink = 0;
unsigned long blinkInterval = 100;
unsigned long powerInterval = 50000; //interval for power to be supplied to NRF24L01 (in ms)

//=====================

void SDfileDate(uint16_t* date, uint16_t* time) { // print a timestamp ("last modified") callback to the SD card
  setSyncProvider(rtc.get);
  *date = FAT_DATE(year(), month(), day());
  *time = FAT_TIME(hour(), minute(), second());
}

//=====================

void oversample(Adafruit_ADS1115 * ads1115Pointer, int oversampleArray[OVERSAMPLE_VALUE], int input) { // Function to oversample ADS1115 pins
  ads1115 = *ads1115Pointer;
  for (int i = 0; i < OVERSAMPLE_VALUE; i++) {
    if ((input == 2) || (input == 3)) {
      int adcValue = ads1115.readADC_SingleEnded(input);
      oversampleArray[i] = adcValue;
    } else {
      int adcValue = ads1115.readADC_Differential_0_1();
      oversampleArray[i] = adcValue;
    }
  }
}

//======================================================================

void setup() {
  Wire.begin(); // Start I2C interface

  Serial.begin(9600);
  while (!Serial) {
    ; // wait for serial port to connect
  }

  pinMode(ledPin, OUTPUT); // initialize LED pin as an output
  digitalWrite(ledPin, ledState); // turn off LED
  pinMode(reedPin, INPUT_PULLUP); // initialize pullup resistor on Reed switch pin
  digitalWrite(reedPin, HIGH); // Set Reed switch pin to HIGH
  dataReceived = 1000; // Set initial blink interval (to be changed by Tx)

  // Setup SD card
  SPI.begin();
  Serial << "Initializing SD card..." << endl;
  if (!sd.begin(chipSelect, SD_SCK_MHZ(12))) {
    Serial << "sd card initialization failed!" << endl;
    sd.initErrorHalt(); // not being able to save data is a terminal error in all cases
  } else {
    Serial << "sd card initialization done." << endl;
  }

  file.open(FILE_NAME, FILE_WRITE);
  if (file) { // If file already exists, don't add a header. If it doesn't exist, then write a header.
    Serial << "File exists, opening file..." << endl;
  } else {
    Serial << "File doesn't exist, creating file and adding header" << endl;
    file << "Date,Time,J1 (mV),J1 oversampled mean (mV),J1 oversampled mean,J1 oversampled min,J1 oversampled max,J1 oversampled sd,J2+ (mV),J3 (mV),J4+ (mV),J4+ oversampled mean (mV),J4+ oversampled mean,J4+ oversampled min,J4+ oversampled max,J4+ oversampled sd,J4- (mV),J4- oversampled mean (mV),J4- oversampled mean,J4- oversampled min,J4- oversampled max,J4- oversampled sd" << endl; // removed "Coin battery (mV)"
  }
  file.close(); // close the file
  while (sd.card() -> isBusy()) {
    ;
  }
  Serial << "Done, file closed." << endl;

  // Initialize the alarms, clear the alarm flags, clear the alarm interrupt flags
  rtc.begin();
  clearClockTrigger();
  enableRTCAlarmsonBackupBattery();
  rtc.setAlarm(DS3232RTC::ALM1_MATCH_DATE, 0, 0, 0, 1);
  rtc.setAlarm(DS3232RTC::ALM2_MATCH_DATE, 0, 0, 0, 1);
  rtc.alarm(DS3232RTC::ALARM_1);
  rtc.alarm(DS3232RTC::ALARM_2);
  rtc.alarmInterrupt(DS3232RTC::ALARM_1, false);
  rtc.alarmInterrupt(DS3232RTC::ALARM_2, false);
  rtc.squareWave(DS3232RTC::SQWAVE_NONE);

  rtc.set(compileTime()); // set the RTC time and date to the compile time (see SRC.h)

  time_t t = rtc.get(); // get the current time
  time_t alarmTime = t + ALARM_INTERVAL;    // calculate the alarm time by adding current RTC time with alarm interval
  formatTime(timestamp, t); // reformat time (see SRC.h)
  Serial << F("Current RTC date and time ") << timestamp << endl;   // print the current time to the serial port

  // set the Alarms
  rtc.setAlarm(DS3232RTC::ALM1_MATCH_HOURS, second(alarmTime), minute(alarmTime), hour(alarmTime), 0); // set Alarm 1 to occur at sampling interval
  rtc.alarm(DS3232RTC::ALARM_1); // clear the alarm flag
  rtc.alarmInterrupt(DS3232RTC::ALARM_1, true);
  rtc.setAlarm(DS3232RTC::ALM2_MATCH_DATE, 0, START_MIN, START_HOUR, START_DAY); // set Alarm 2 to occur at specific date and time
  rtc.alarm(DS3232RTC::ALARM_2); // clear the alarm flag
  rtc.alarmInterrupt(DS3232RTC::ALARM_2, true);
  extInterrupt(intPin); //create interrupt source on Interrupt Pin

  //Setup ADC 1015 and 1115
  Serial << "Getting differential reading from AIN0 (P) and AIN1 (N)" << endl;
  Serial << "ADC Range: +/- 0.512V (1 bit = 2mV)" << endl;
  ads1015.setGain(ADS1015_GAIN_VAL); // set Gain for ADC 1015
  ads1015.begin(0x48); // Initialize ads1015 at the default address 0x48
  Serial << "Getting differential reading from AIN0 (P) and AIN1 (N)" << endl;
  Serial << "ADC Range: +/- 1.024V (1 bit = 0.03125mV)" << endl;
  ads1115.setGain(ADS1115_GAIN_VAL); // set Gain for ADC 1115
  ads1115.begin(0x49); // Initialize ads1115 at address 0x49

  //Setup Radio
  radio.begin();
  //radio.enableAckPayload(); // DO I NEED TO HAVE THIS, YEAH?
  loadFileData(); // pre-load Ack Payload
  Serial << "Powering down radio" << endl;
  radio.powerDown(); // immediately power down the radio until reed switch trigger

  //LowPower.sleep(); // go to sleep until Alarm is triggered. This will break Serial communications, but the loop will still be running.
}

//================

void loop() {
  reedState = digitalRead(reedPin);
  if (reedState == LOW) {
    reedTriggered();
  }
  if (triggerState == true ) {
    radioTriggered();
  }
  if (!digitalRead(intPin)) { // check to see if the INT/SQW pin is low, i.e. an alarm has occurred
    if (Serial) {
      Serial << "starting data collection..." << endl;
    }
    if (!radioPowerState) { // only collect new data if NRF24L01 is powered down
      collectData();
    }
  }
}

//======================================================================

void blinkWithoutDelay() {
  unsigned long currentMillisBlink = millis();
  if (currentMillisBlink - previousMillisBlink >= blinkInterval) {
    previousMillisBlink = currentMillisBlink; // update previousMillis value
    if (ledState == LOW) {
      ledState = HIGH;
    } else {
      ledState = LOW;
    }
    digitalWrite(ledPin, ledState);
  }
}

//======================================================================

void collectData() {
  if (rtc.alarm(DS3232RTC::ALARM_2) ) {    // check alarm flag, clear it if set
    alarmTrigger = true; // set alarm trigger to TRUE to trigger Alarm 1
    time_t t = rtc.get();
    formatTime(timestamp, t);
    if (Serial) { //
      Serial << "ALARM_2 " << timestamp << endl; // print the time when this part of the loop is running
    }
  }

  if (alarmTrigger && rtc.alarm(DS3232RTC::ALARM_1)) { // check alarm flag (and clear the flag if set)
    blinkWithoutDelay(); // Blink LED to indicate data is being collected
    time_t t = rtc.get(); // get the current time
    formatTime(timestamp, t);
    time_t alarmTime = t + ALARM_INTERVAL; // calculate the next alarm time
    rtc.setAlarm(DS3232RTC::ALM1_MATCH_HOURS, second(alarmTime), minute(alarmTime), hour(alarmTime), 0); // set the alarm
    if (Serial) {
      Serial << "IT'S TIME TO SAMPLE! " << timestamp << endl; // print the time when this part of the loop is running
    }
    SdFile::dateTimeCallback(SDfileDate); // Set file date and time on sd card ("last modified"). Check out this page if having issues: https://arduino.stackexchange.com/questions/39126/how-does-one-set-attributes-for-sd-files
    file.open(FILE_NAME, FILE_WRITE); // open the file. note that only one file can be open at a time, so you have to close this one before opening another.

    if (file) { // if the file opened okay, write to it:
      if (Serial) {
        Serial << "Writing to SD Card..." << endl;
      }
      time_t TIME = rtc.get();
      file << month(TIME) << "/" << day(TIME) << "/" << year(TIME) << "," << hour(TIME) << ":" << minute(TIME) << ":" << second(TIME) << "," ;
      readADC();
      // close the file:
      file.close();
      while (sd.card() -> isBusy()) {
        ;
      }
    } else {
      if (Serial) {
        Serial << "error writing to file" << endl; // if the file didn't open, print an error:
      }
    }
    digitalWrite(ledPin, LOW); // turn off LED
  }
  if (Serial) { // end the Serial connection if port is available
    Serial << "Going to sleep..." << endl;
    //Serial.flush();
    Serial.end();
  }
  //LowPower.sleep(); // go to sleep until next Alarm is triggered. This will break Serial communications, but the loop will still be running.
}

//======================================================================

void extInterrupt(int intPin) {
  pinMode(intPin, INPUT_PULLUP);
  LowPower.attachInterruptWakeup(digitalPinToInterrupt(intPin), wakeUp, CHANGE);
}

//======================================================================
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

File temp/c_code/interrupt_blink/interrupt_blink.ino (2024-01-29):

#include <SPI.h>
#include <Wire.h>

#include "ArduinoLowPower.h"
#include <DS3232RTC.h>      // https://github.com/JChristensen/DS3232RTC
#include <Streaming.h>      // https://github.com/janelia-arduino/Streaming , allows you to use << formatting
#include <Time.h>           // https://github.com/PaulStoffregen/Time
#include "SdFat.h"          // Adafruit fork of SdFat library by https://github.com/greiman/SDFat

#include "CONFIG.h"
#include "SRC.h"

DS3232RTC rtc;            // Construct RTC
SdFat sd;                 // Create the objects to talk to the SD card
SdFile file;          // Construct File for SD card
#define DS3231_I2C_ADDRESS 0x68 // Needed when we cut VCC line from RTC, see https://github.com/EKMallon/Utilities/blob/master/setTme/setTme.ino
#define DS3231_CONTROL_REG 0x0E

const int ledPin = LED_BUILTIN;
int ledState = LOW; // ledState used to set the LED
char timestamp[32]; // Current time from the RTC in text format, 32 bytes long
bool alarmTrigger = false; // Create variable set to false for alarm nesting. Set to true if you want immediate start time.
const byte intPin = 5; // RTC provides an alarm signal on this pin
//volatile boolean clockInterrupt = false;

//#define CLOCK_POWER A2;
const uint8_t chipSelect = 4; // Adalogger microSD card chip select pin
int readPin1 = A1; //J1+
int Val1 = 0;
float Volt1 = 0;

void setup() {
  //delay(1000); //delay so we can see normal current draw
  pinMode(LED_BUILTIN, OUTPUT); // initialize digital pin 13 as an output (blink)
  digitalWrite(LED_BUILTIN, LOW); // turn off LED
  pinMode(readPin1, INPUT);

  Wire.begin(); // Start I2C interface
  Serial.begin(115200);
  while (!Serial) {
    ; // wait for serial port to connect. Needed for native USB port only
  }

  // Setup SD card
  Serial << "Initializing SD..." << endl;

  // change to SPI_FULL_SPEED for more performance.//change to SPI_HALF_SPEED for old cards -half speed like the native library.
  if (!sd.begin(chipSelect, SD_SCK_MHZ(12))) {
    Serial << "sd card initialization failed!" << endl;
    Serial.flush();
    sd.initErrorHalt(); // not being able to save data is a terminal error in all cases
  }

  file.open("datafile.txt", FILE_WRITE);
  if (!file) {
    Serial.println("Failed to open file!");
    return;
  }
  file.println("Hello world!");
  file.close();

  Serial << "sd card initialization done." << endl;

  // Set up RTC
  Serial << "Initializing rtc..." << endl;

  rtc.begin();
  //setSyncProvider(rtc.get); // Time and date are set to date and time on your computer at compiletime
  clearClockTrigger();
  enableRTCAlarmsonBackupBattery();
  rtc.setAlarm(DS3232RTC::ALM1_MATCH_DATE, 0, 0, 0, 1); //initialize alarms
  rtc.setAlarm(DS3232RTC::ALM2_MATCH_DATE, 0, 0, 0, 1);
  rtc.alarm(DS3232RTC::ALARM_1); // clear alarm flags
  rtc.alarm(DS3232RTC::ALARM_2);
  rtc.alarmInterrupt(DS3232RTC::ALARM_1, false); //clear alarm interrupt flags
  rtc.alarmInterrupt(DS3232RTC::ALARM_2, false);
  rtc.squareWave(DS3232RTC::SQWAVE_NONE);

  rtc.set(compileTime()); // set the RTC time and date to the compile time (see SRC.h)

  time_t t = rtc.get(); // get the current time
  time_t alarmTime = t + ALARM_INTERVAL;    // calculate the alarm time by adding current RTC time with alarm interval
  formatTime(timestamp, t); // reformat time (see SRC.h)
  Serial << F("Current RTC date and time ") << timestamp << endl;   // print the current time to the serial port
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

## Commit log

2022-12-16 move over files to new repo
    [1214TRIS.CSV, 1214_tris_madge.csv]
2022-12-16 append identifying information, select single calibration value
2022-12-16 compare arduino tolerance values
2022-12-17 fix filter by date_time.
2022-12-17 fix filter by date_time, compare HOBO and loggers.
2022-12-17 run temperature correction date to plot.
2022-12-17 add geom_ribbon to plot tris calibration data comparison.
2022-12-17 apply correction equation to arduino data.
2022-12-19 plot data pre-subset with correct date/time and plot sensor swap data.
2022-12-19 raw data, cleaned for correct start/end date and time.
    [1215DEPL.CSV, 1215TRIS.CSV, 1215_deploy_madge.csv, 1215_tris_madge.csv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]
2022-12-20 plot differences between swapped sensors, clean up lag data to get accurate numbers.
2022-12-20 Lag field deployment data to get sensor measurement differences.
2022-12-20 double check sensors are in order before lag().
2023-03-25 apply calibration coefficients (using HOBO temp data) to deployment and calibration data
2023-03-25 compare madgetech/arduino reads during sensor swap
2023-03-25 compare reads against HOBO temperature data to calculate correction coefficients for each sensor
2023-03-25 calculate temperature correction coefficients for each collected date/temperature
2023-03-25 apply HOBO temperature correction coefficients to deployment data
2023-03-25 raw data for sensor swap
    [1216TRIS_swap.CSV, 1216_tris_madge_swap.csv]
2023-03-25 Dec 2022 sensor swap prelim visualization figures
2023-03-25 HOBO temperature data from Dec 2022 sensor tests
    [1215_hobo_depl.csv, 1215_hobo_tris.csv, 1216_hobo_tris.csv, 1219_hobo_tris.csv]
2023-03-25 Dec 2022 tables for HOBO temperature correction plotting
    [hobo_correction.csv, logger_correction-arduino.csv, logger_correction-madgetech.csv]
2023-03-25 add all calibrated data
    [1214TRIS_arduino_omegas.csv, 1214TRIS_arduino_omegas_calib.csv, 1214TRIS_arduino_omegas_minus.csv, 1214TRIS_arduino_omegas_minus5.csv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]
2023-03-25 Dec 2022 raw sensor swap figures
2023-03-25 march 2023 re-analysis sensor swap figure tests
2023-03-27 Add Read/Write ADC inputs, successful compile with printing timestamp to SD card.
2023-03-27 Successful print timestamp callback to SD card; Change serial and df print to Streaming format
2023-04-02 Print to SD card.
2023-04-03 Justify oversampling and oversampling rate
    [0402_16X.CSV, 0402_256.CSV, 0402_64X.CSV]
2023-04-04 SIMPLIFY to only oversample one pin to test current draw for each oversampling event.
2023-04-08 first half testing arduino/madgetech in lab
    [0407_10S.CSV, 0407_25C.CSV, 0407_25S.CSV, madge-25-10.xlsx]
2023-04-08 add lab data from 4.8
    [0407_18.CSV, MADG-4.8.xlsx]
2023-04-10 add ice cold data.
    [0409ICE.CSV, MADG-4.9.xlsx]
2023-04-10 oversample comparison data.
    [OVERSAMP.CSV]
2023-04-10 add lab data madgetech 4.10.
    [MADG-4.10_GREEN.xlsx, MADG-4.10_RED.xlsx]
2023-04-12 4.11 swap data.
    [411SWAP.CSV, MADG-4.10_GREENovernight.xlsx, MADG-4.10_REDovernight.xlsx, MADG-4.11_Green-Red-ardswap.xlsx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]
2023-04-13 add arduino day 4.12 data
    [412ARD0.CSV]
2023-05-22 upload all arduino c code
2023-05-22 upload first pass cleaned up Arduino code
2023-05-22 move files over to draft folder
    [0402_16X.CSV, 0402_256.CSV, 0402_64X.CSV, 0407_10S.CSV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]
2023-08-16 ignore draft_files/.
    [412ARD0.CSV, CORRECTED_converted-cold.csv, CORRECTED_converted-hot.csv, CORRECTED_converted-room.csv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]
2023-08-16 gitignore draft_files/.
    [412ARD0.CSV, CORRECTED_converted-cold.csv, CORRECTED_converted-hot.csv, CORRECTED_converted-room.csv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]
2023-08-16 rename draft_files/ to temp/ and gitignore.
    [0402_16X.CSV, 0402_256.CSV, 0402_64X.CSV, 0407_10S.CSV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]
2023-09-26 it "works" but still consuming a lot of power
2023-10-13 Add code drafts (since wireless added)
2023-11-03 add first draft KiCAD files
    [test_voltdiv.kicad_pcb, test_voltdiv.kicad_sch]
2024-01-13 V1 JLCPCB design
    [ph-sensor-B_Cu.gbl, ph-sensor-B_Mask.gbs, ph-sensor-B_Paste.gbp, ph-sensor-B_Silkscreen.gbo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]
2024-01-22 update pcb schematic/design
    [new_proj-B_Cu.gbl, new_proj-B_Mask.gbs, new_proj-B_Paste.gbp, new_proj-B_Silkscreen.gbo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]
2024-01-26 add comparison data and write up code
    [0123comp.csv, 0123comp_clean.csv, 0125tris.csv, 0125tris_clean.csv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]
2024-01-26 compare 36 hours data, adjusted SeaFET with Arduino design
    [0125tris_clean_omegas.csv, 0125tris_clean_omegas_calib.csv, FINAL_arduino.csv, SeaFET2-0002300-Data-20240125T211850-TRIS.csv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]
2024-01-27 Generate fake data to measure transmission packet loss rate
    [sequence.csv, zeroes.csv]
2024-01-29 View power consumption with V2 code/hardware
    [PreDataCollectionData.csv, VoltageSet3_60V_at2023_10_14_12_19_57.csv, VoltageSet3_60V_at2023_10_14_12_25_20.csv, VoltageSet3_60V_at2023_10_14_12_27_18.csv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]
2024-01-31 overwrite in-between periods with sleep current, add triangles for reed switch activation
2025-04-06 update sensor swap figures for publication in dissertation
2025-04-06 update current consumption fig for dissertation
